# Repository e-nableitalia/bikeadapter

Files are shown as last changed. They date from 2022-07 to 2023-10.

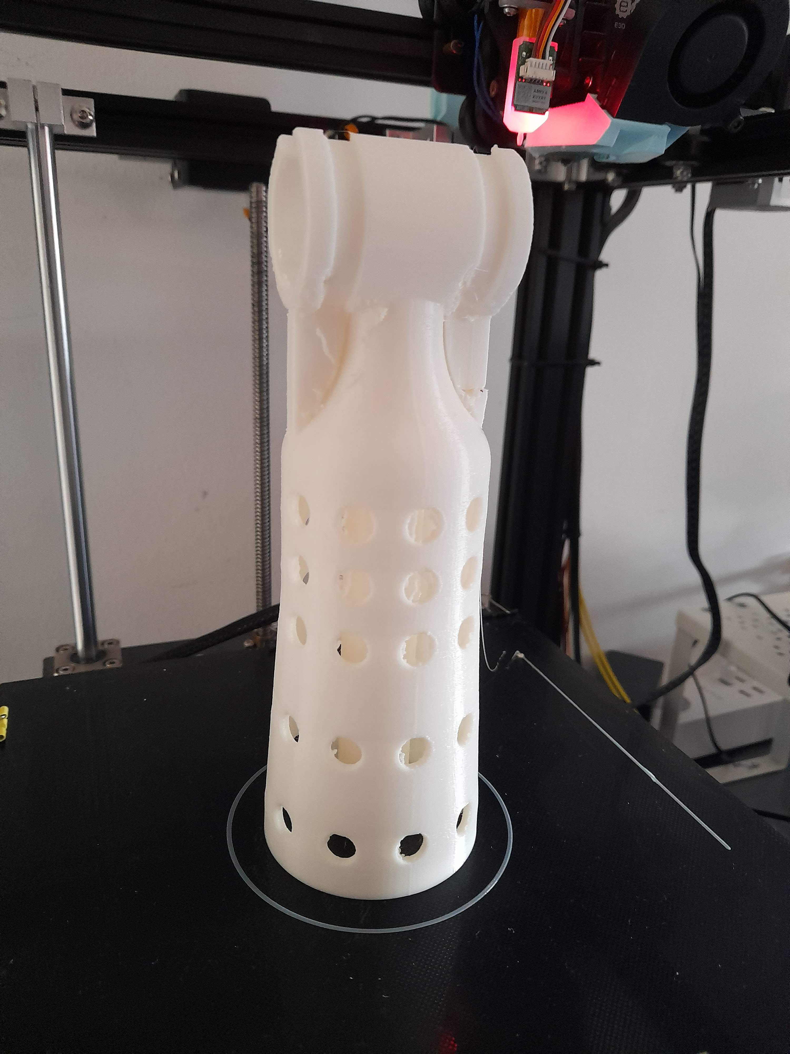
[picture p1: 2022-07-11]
pictures/Print-test.jpg

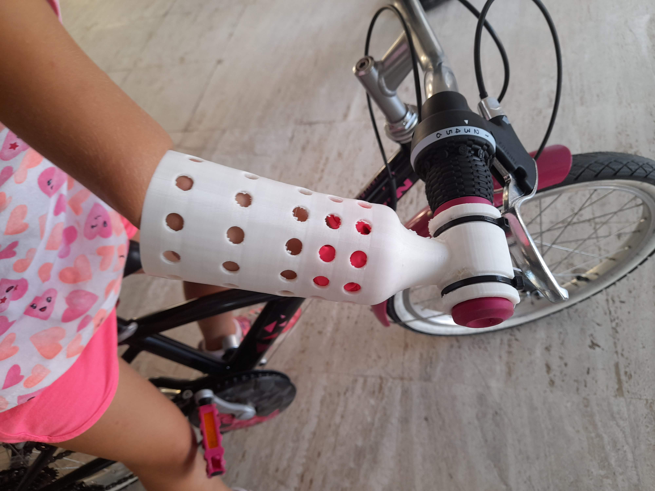
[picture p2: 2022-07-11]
pictures/Assembly-1.jpg

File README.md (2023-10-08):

## bikeadapter

A bike adapter device for children with limb difference problems, configurable to be adapted to the user, can be entirely build with a 3d printer using a flexible filament

## Description

After several iteraction the e-Nable Italia's team composed by Alessandro and Michele has released the first prototype of a hand device called "Bike Adapter".

This device was designed to help children and adults with limb difference problems (amputations or agenesys of hand/arm) to easly connect with the bicycle handlebar allowing a better control of the bike direction.

Fusion version is deprecated and was left here only for historical reason, we suggest to to build your device using the last stable version published on OnShape by e-Nable Italia (See OnShape project below).

The device is printed with flexible filament (TPU) to obtain the perfect mix between comfort, safety and functionality.
The project is open source, e-Nable Italia's volunteers provide the Bike Adapter device (and others) free of charge for anyone is in need of such assistive devices.

## History

Up to Rev. 18v6 of the project the Bike Adapter was entirely designed with Autodesk Fusion360 and can be customized setting the approriate values in the available parameters allowing the generation of a 3d model adapted to the end user and thus STL or 3MF files for the slicer/3d printer.

Since Rev. 19 the project was moved on OnShape and project version numbering was restarted.

## OnShape project

* [Stable release](https://cad.onshape.com/documents/ca8363f0e231780e668e998b/w/a26bb6ec5623c8082f0c169f/e/3e5b5222f11b40dd3fc85b5d) - Manteined by e-Nable Italia

> [!IMPORTANT]
> This project is parametric and requires specific recipient adaptation, see **dimensioning** section for details.

## Version history

* [OnShape V3](https://cad.onshape.com/documents/ca8363f0e231780e668e998b/w/a26bb6ec5623c8082f0c169f/e/3e5b5222f11b40dd3fc85b5d) - reinforced structure, added internal hole to double perimeters surface and to increase flexibility, new design significatively decreases print time
* [OnShape V2](https://cad.onshape.com/documents/5b587ad656e9d002f8e6bad6/w/de2c6c2802ab923db649ef32/e/ab629266e0f6758e30a87845) - added multiple supports
* [OnShape V1](https://cad.onshape.com/documents/46a4c4172ddd04c75d593001/w/5926f7823c4074041b5158a1/e/589555b9dba7eac6af07f0b4) - first release, single support

* [Development release](https://cad.onshape.com/documents/e225086690158d5a937bf9fe/w/4021bf2bfacdceba3b1f0556/e/9dfe74fe60fd68384dbb2f50) - Mantained by Alessandro Villa

## Thingiverse project

the project was also published on Thingiverse at the following link: [Bike Adapter](https://www.thingiverse.com/thing:5422603)

## Dimensioning

Dimensioning is done by setting appropriate values in parameters exposed in the OnShape project.

An online configurator tool is available at the following address: [Bike Adapter Configurator](https://dev.e-nableitalia.it/configurator/)

Manual dimensioning can be done by inserting the appropriate values in the OnShape Feature panel.
Insert the values in the parameters in sequence:
* A_lng_unaff, length of unaffected arm
* B_lng_affect, length of affected arm
* C_tip_circ, circumference length, measured approximately 2 cm below the tip of the stump
* D_root_circ, circumference length, measured at the elbow crease
* E_handle_dia, bike handlebar diameter
* F_lng_affect_inner_elbow, length of affected arm, measured from elbow crease to the tip of the stump
* vent_hole_no, number of vent holes, take care to choose an appropriate value to keep holes below the solid body of the device

Detailed instructions for dimensioning the device can be found [here](https://e-nableitalia.it/en/dimensionamento-bike-adapter/)

## Printing directives

* Rafts: No 
* Supports: No 
* Resolution: 0.2 
* Infill: 15% - Gyroid
* Filament brand: Ninjaflex 
* Filament color: Whater Translucent (#3DNF0829005), this material has proven to be the most realiable and with better layer adhesion (compared to other colors and filament brands we evaluated)
* Filament material: TPU, suggested shore 85a, higher shore gives more rigidity, use lower for additional flexibility for the device.

## Authors

Michele Praga - pragamichele@gmail.com

Alessandro Villa - filotto78@gmail.com

e-Nable Italia - info@e-nableitalia.it 

Check for further information, updates and information on this and other e-Nable Italia’s projects on our website: [https://e-nableitalia.it/bikeadapter](https://e-nableitalia.it/it_it/portfolio/bike-adapter/) & https://e-nableitalia.it

## License

This material is released under *Creative Commons - Attribution - Non-Commercial - Share Alike license*

## LIMITATION OF LIABILITY.

UNDER NO CIRCUMSTANCES AND UNDER NO LEGAL THEORY, WHETHER TORT (INCLUDING NEGLIGENCE), CONTRACT, OR OTHERWISE, SHALL YOU, THE INITIAL DEVELOPER, ANY OTHER CONTRIBUTOR, OR ANY DISTRIBUTOR OF COVERED CODE, OR ANY SUPPLIER OF ANY OF SUCH PARTIES, BE LIABLE TO ANY PERSON FOR ANY INDIRECT, SPECIAL, INCIDENTAL, OR CONSEQUENTIAL DAMAGES OF ANY CHARACTER INCLUDING, WITHOUT LIMITATION, DAMAGES FOR LOSS OF GOODWILL, WORK STOPPAGE, COMPUTER FAILURE OR MALFUNCTION, OR ANY AND ALL OTHER COMMERCIAL DAMAGES OR LOSSES, EVEN IF SUCH PARTY SHALL HAVE BEEN INFORMED OF THE POSSIBILITY OF SUCH DAMAGES. THIS LIMITATION OF LIABILITY SHALL NOT APPLY TO LIABILITY FOR DEATH OR PERSONAL INJURY RESULTING FROM SUCH PARTY'S NEGLIGENCE TO THE EXTENT APPLICABLE LAW PROHIBITS SUCH LIMITATION. SOME JURISDICTIONS DO NOT ALLOW THE EXCLUSION OR LIMITATION OF INCIDENTAL OR CONSEQUENTIAL DAMAGES, SO THIS EXCLUSION AND LIMITATION MAY NOT APPLY TO YOU.

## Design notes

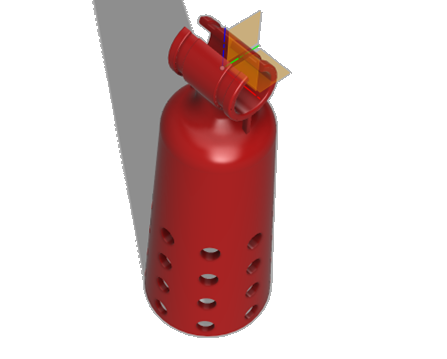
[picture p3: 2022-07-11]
pictures/BikeAdapter_Colorato.png

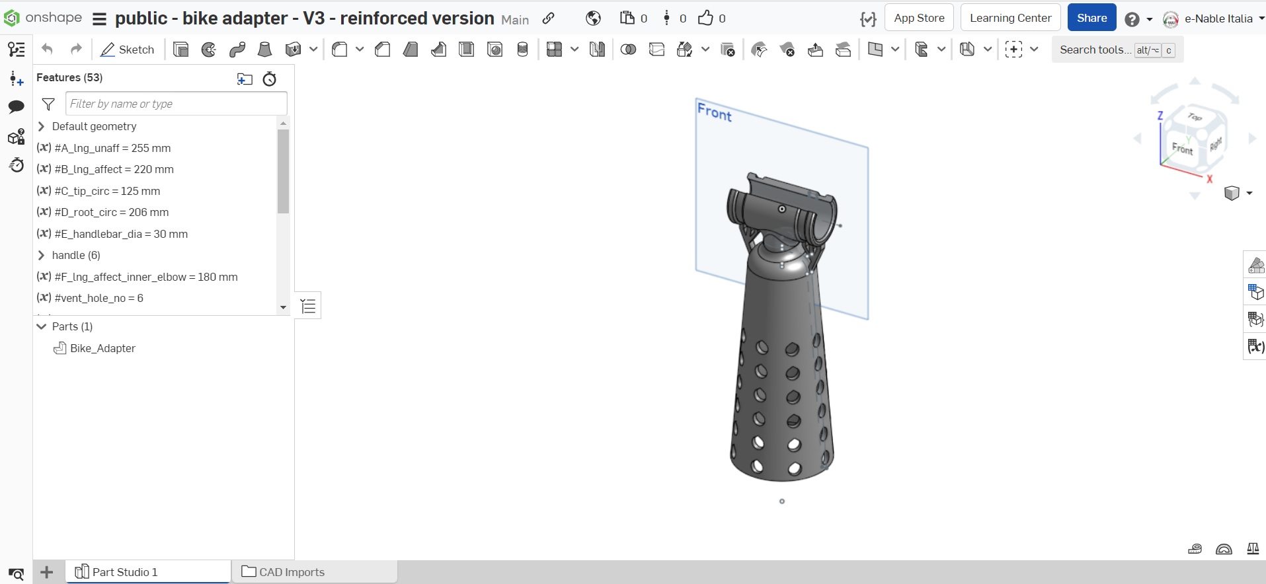
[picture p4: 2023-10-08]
pictures/BikeAdapter_Dimensioning.jpg

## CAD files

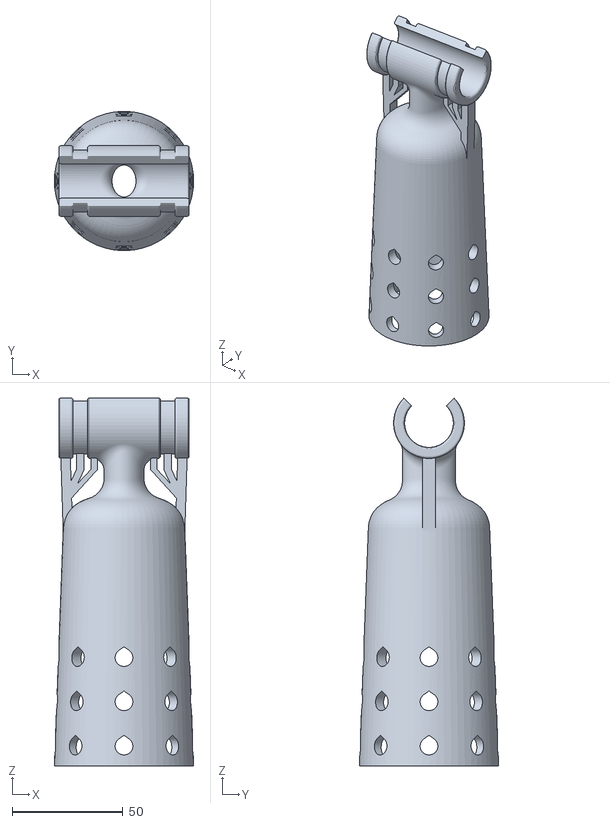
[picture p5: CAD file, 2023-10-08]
Bike_Adapter_Example.stl
63.0 x 62.9 x 166.3

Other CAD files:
Bike Adapter-v18.f3d
OLD_Version/Bike Adapter-v18.f3d

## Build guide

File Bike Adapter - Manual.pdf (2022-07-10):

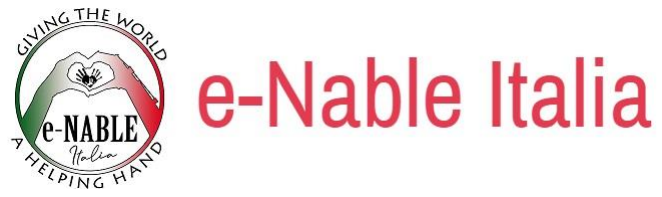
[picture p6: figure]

# Bike Adapter

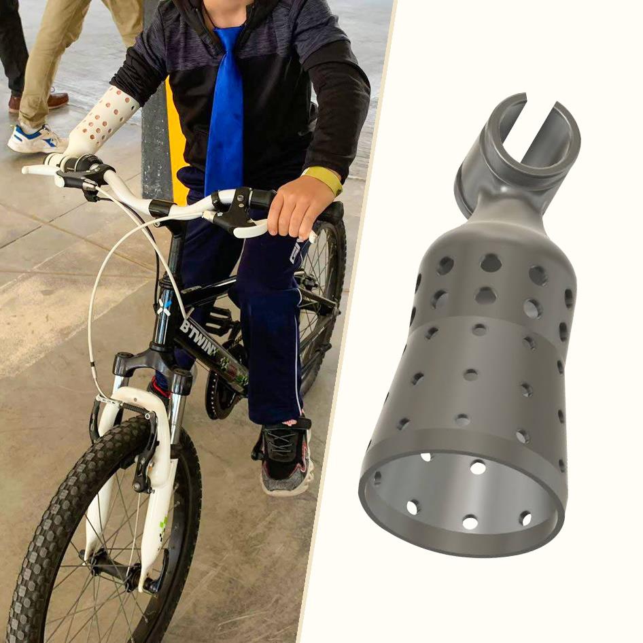
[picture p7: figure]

## A bike adapter device for children with limb difference problems, configurable to be adapted to the user, can be entirely build with a 3d printer using a flexible filament

# By Michele Praga – Alessandro Villa

Bike Adapter by e-Nable Italia is licensed under the Creative Commons - Attribution - Non-Commercial - Share Alike (https://creativecommons.org/licenses/by-nc-sa/4.0/) license.

Rev. 1.0 – 220711

Michele Praga - pragamichele@gmail.com, Alessandro Villa - filotto78@gmail.com, e-Nable Italia - info@e-nableitalia.it

Check for further information, updates and information on this and other e-Nable Italia’s projects on our
website: https://e-nableitalia.it/bikeadapter & https://e-nableitalia.it

## Contents

### 1. Disclaimer | 3

### 2. Basic Info | 4

### 3. Links | 6

### 4. Makers | 7

### 5. Educational | 8

### 6. Engineering (Device Sizing) | 9

### 7. Assembly | 12

### 8. Lists & Media | 13

# 1.Disclaimer

The Bike Adapter design is being released under Creative Commons - Attribution - Non-Commercial - Share Alike (https://creativecommons.org/licenses/by-nc-sa/4.0/) 4.0 International (CC BY-NC-SA 4.0) open-source license to encourage further innovation in this field, and improve global access to assistive technology.

This design is released for trial and evaluation purposes only, and it is intended to benefit certain individuals with specific arm differences and is not intended, and shall not be used, for commercial purposes.

The acceptance of this design by e-Nable Italia, and any such information provided by the design team is presented as is without representation or warranties of any kind, express or implied, and is intended to be a free gift to recipients for the sole purpose of evaluating various design iterations, ideas and modifications.

The Bike Adapter must be used for only light biking activities, and not for any severe tasks like off-road or competitive events. Any individual associated with e-Nable Italia and e-Nable Italia itself shall not be liable for any injuries or damages resulting from the use of any information or designs provided.

The Bike Adapter is experimental device, it is not classified as a medical device, and it is for evaluation purposes only. In some cases, these devices will not be appropriate for each individual, and consultation with medical professionals and occupational therapists must be sought and obtained before use.

# 2.Basic Info

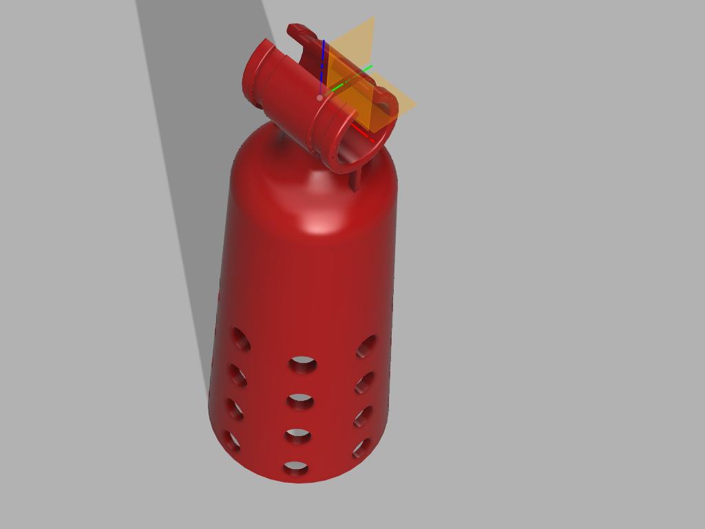
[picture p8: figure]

Authors: Michele Praga and Alessandro Villa

Device type: Arm

Minimum user needs: A functioning forearm

Type of device: Mechanical

Maturity | Cost of Materials | Popularity | Assembly difficulty | Grip Strength

N/A

To learn about what each of the above icons represents, please refer to the Device Ratings Guide. (https://hub.e-nable.org/s/chapter-spotlight/wiki/page/view?title=Project+Ideas+%26+Suggestions#null)

Development status: In validation

Basic data

- Number of parts: 1
- Assembly time (estimated): 0.5 hrs
- Store-bought parts: zip cable ties
- Number of known builds: 3

- Grip type: none
- Actuation type: no actuation
- Scalability: STL or 3MF is generated by Autodesk Fusion360 using parameters

Basic description

This device is intended to be connected to the bike handlebar through zip ties. The elasticity of the joint ensures an adequate mobility for steering.

License: Creative Commons Attribution-NonCommercial-ShareAlike 4.0 International (CC BY-NC-SA 4.0)

Credit and Contributions: missing credit

# 3.Links

Main STL Files: https://www.thingiverse.com/thing:5422603

Git Hub: https://github.com/e-nableitalia/bikeadapter

Major Modifications: 🔴

You can request a modification in the comments below

Source Files: Fusion360 file in download area

Instructionals: An instructional document is available with in download area

Editors and Customizers: See details below for info on device customization

# 4.Makers

missing photo of made device 🔴

Bill of Materials

- Cable zip ties
- TPU filament

Tools: cut plier

Recommended print settings:

Rafts:
No

Supports:
No

Resolution:
0.2

Infill:
60%

Filament brand:

Ninjaflex

Filament color:

N/A

Filament material:

TPU, suggested shore 85a, higher shore gives more rigidity, use lower for additional flexibility for the device.

Device advantages: Simplicity

# 5.Educational

After several design iterations, the e-Nable Italia team released the first prototypes of what is simply called “Bike Adapter”.

The device is designed in Autodesk Fusion360 that is free for hobbyists, non-commercial use, and for qualifying startups.

In the parameter window, the user inputs some dimensions of unaffected and affected arm, and the software automatically generate the 3D model.

The Bike Adapter design is being released under a Creative Commons Attribution-Non Commercial-ShareAlike 4.0 International (CC BY-NC-SA 4.0) open-source license to encourage further innovation in this field, and improve global access to assistive technology.

This design is released for trial and evaluation purposes only, and it is intended to benefit certain individuals with specific arm differences and is not intended, and shall not be used, for commercial purposes.

The acceptance of this design by e-Nable Italia, and any such information provided by the design team is presented as is without representation or warranties of any kind, express or implied, and is intended to be a free gift to recipients for the sole purpose of evaluating various design iterations, ideas and modifications. The Bike Adapter must be used for only light biking activities, and not for any severe tasks like off-road or competitive events. Any individual associated with e-Nable Italia and e-Nable Italia itself shall not be liable for any injuries or damages resulting from the use of any information or designs provided. The Bike Adapter is experimental device, it is not classified as a medical device, and it is for evaluation purposes only. In some cases, these devices will not be appropriate for each individual, and consultation with medical professionals and occupational therapists must be sought and obtained before use.

The Bike Adapter has been designed using Autodesk Fusion 360.

No historical credits available.

Further Information

Check for further information, updates and information on this and other e-Nable Italia’s projects on our website: https://e-nableitalia.it/bikeadapter & https://e-nableitalia.it

# 6.Engineering (Device Sizing)

Only five parameters are needed to properly size the device.

A – unaffected forearm length (Figure 1)

B – affected forearm length (Figure 2)

C – tip stump diameter

D – root stump diameter

E – Handle diameter (Figure 3)

An additional parameter, the number of venting holes, could be modified according to the length of the stump wall.

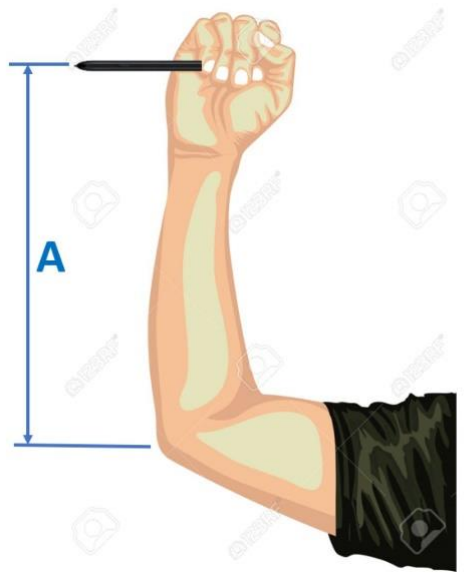
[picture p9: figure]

Figure 1 - Measure of unaffected arm

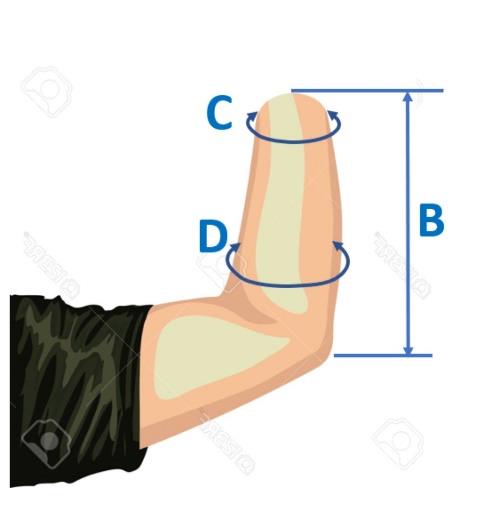
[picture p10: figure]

Figure 2 - Measure of affected arm

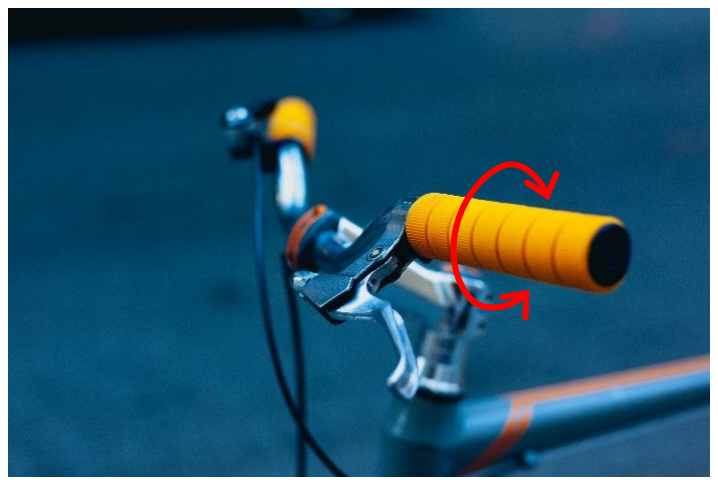
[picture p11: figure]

Figure 3 - Measure of handlebar

Dimensioning is done by setting appropriate values in parameters exposed in the Autodesk Fusion360 project (Figure 4). After opening the project in Autodesk Fusion360 go to "Modify" menu and select "fx Change Parameters" menu entry.

Insert the appropriate values in the parameters window.

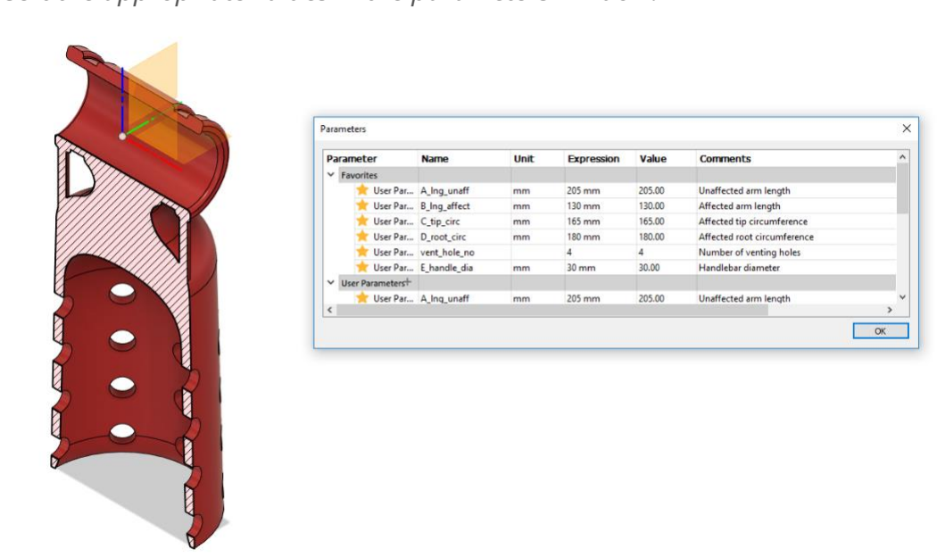
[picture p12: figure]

Figure 4 - Parameter window

The file is designed in a way in which the walls thickness is inversely proportional to the length of the affected arm, to provide necessary lateral stability.

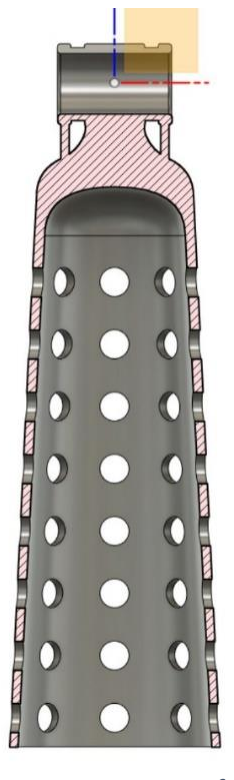
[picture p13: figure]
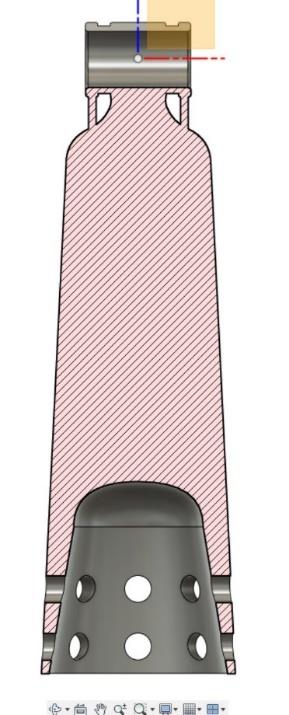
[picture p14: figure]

Figure 5 - Short stump configuration | Figure 6 - Long stump configuration

The grip on the bike handlebar is ensured by the frictions between TPU and rubber handles. The handle grip pillow has two slots to keep in position the two cable zip ties.

Known issues and solutions

no issues have been reported

Do you know of an issue with this device? Do you have a solution for a common issue? Do you have a suggestion for an improvement? Please report it to the development team at the following address: info@e-nableitalia.it 🔴

Help resources

If you are not familiar with Fusion360, you can contact e-Nable Italia team at the following e-mail address: info@e-nableitalia.it, asking to generate the STL or 3MF file for you, please provide the five mentioned dimensions/measures required to make a properly dimensioning of the device.

Requested Modifications

no modifications have been requested at this point

# 7.Assembly

Connect the Bike Adapter device to the bike handlebar, rotate the device accordingly to ensure a comfortable positioning of the arm into the device (usually an angle of approx. 30° with the ground plane is adequate).

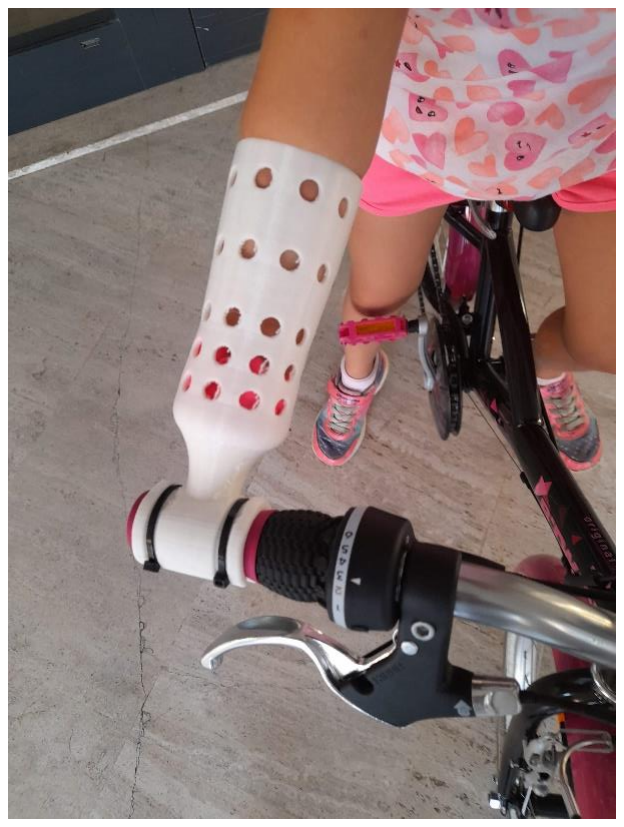
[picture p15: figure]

Secure the device with the cable zip ties, cut the exceeding part of the zip ties and ensure the device is well connected to the handlebar: move the terminal part of the device (the part that connects to the arm) up and down to ensure there is no rotation of the device on the handlebar.

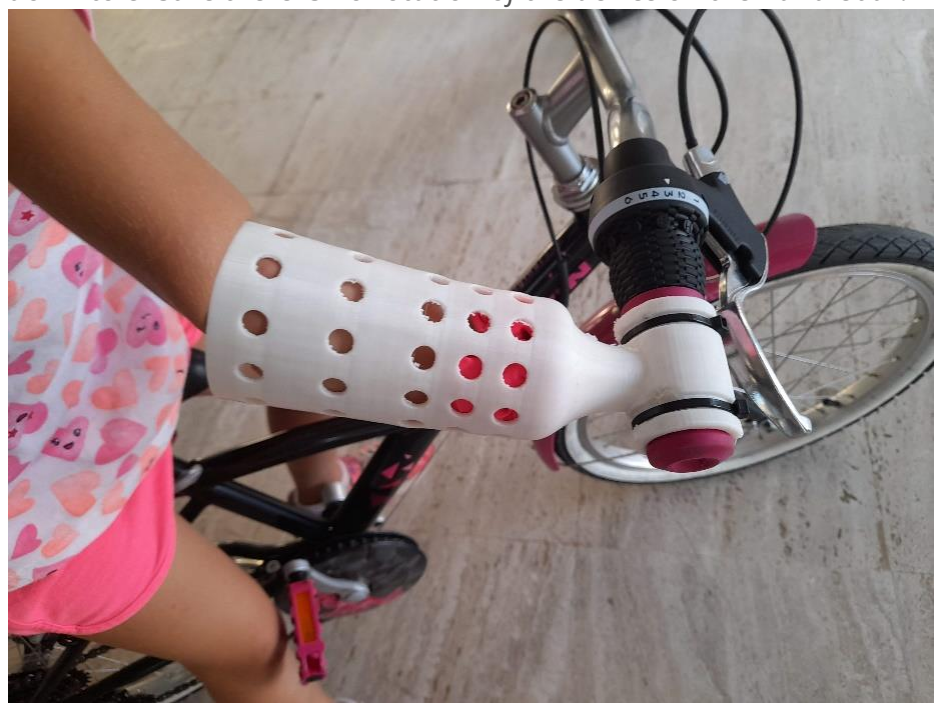
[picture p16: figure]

# 8.Lists & Media

Media links: no links available 🔴

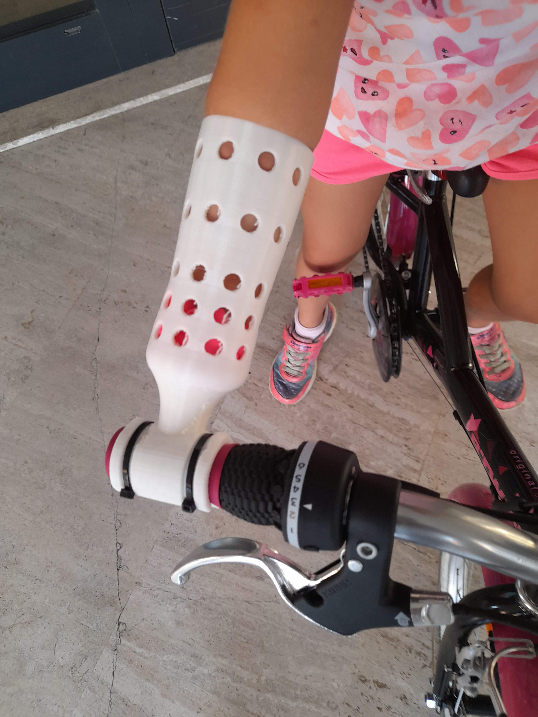
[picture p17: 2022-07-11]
pictures/Assembly-2.jpg

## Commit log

2022-06-28 Added fusion project and e-nable device template
    [bike adapter conico v16.f3d]
2022-06-30 updated device template
2022-07-10 review of doc and filename
    [Bike Adapter-v16.f3d]
2022-07-10 Manual: added photo to assembly section
2022-10-05 Added V18
    [Bike Adapter-v16.f3d, Bike Adapter-v18.f3d]
2023-10-08 Updated description, moved fusion project in OLD_Version folder
    [Bike Adapter-v18.f3d]
2023-10-08 added sample stl, fixed description in readme (configurator url) and added dimensioning picture
    [Bike_Adapter_Example.stl]
